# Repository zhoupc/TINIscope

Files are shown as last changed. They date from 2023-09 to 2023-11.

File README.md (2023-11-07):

# TINIscope 

<!-- **Tightly integrated neuronal imaging fluorescence microscope** -->

<!-- <img src="./assets/demo_video.gif" alt="animation of neural activity recorded in a mouse using the TINIscope" width="300" align="right" /> -->
simultaneous calcium imaging in 4 hippocampal regions of a mouse

In this project repository, we introduce TINIscope, a **Tightly Integrated Neuronal Imaging microscope** optimized for electronic and opto-mechanical design. With its compact and lightweight design of 0.43 g, TINIscope enables unprecedented simultaneous imaging of behavior-relevant activity in up to four brain regions in mice. Moreover, TINIscope can be combined with additional modules to facilitate optogenetics, electrical stimulation, or local field potential recordings, allowing for multi-modal experimental design. Overall, TINIscope represents a timely and indispensable tool for studying the brain-wide interregional coordination that underlies unrestrained behaviors.

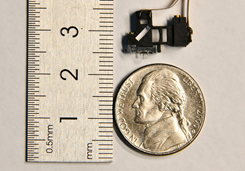
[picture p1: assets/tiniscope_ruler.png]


## Features

TINIscope features an ultra-compact size and an incredibly light weight, enabling the option to wear four of them on a single mouse. The key specifications are outlined below:

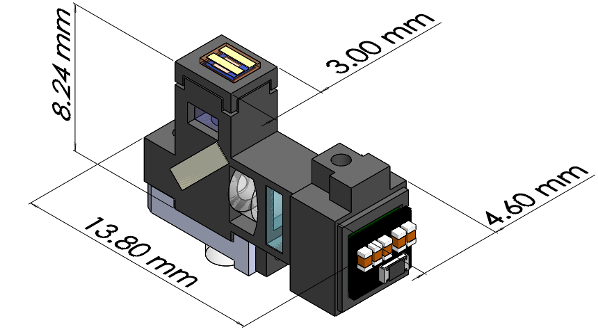
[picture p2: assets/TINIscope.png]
dimension of one TINIscope


| Specications                | Value            |
| --------------------------- | ---------------- |
| Field of view(FOV)          | 450 × 450  μm    |
| Weight of single unit       | 0.43g            |
| Dimensions                  | 4.6×13.8×8.24 mm |
| Typical oprating frame rate | 40 Hz            |
| Optical resolution          | 2.2 μm           |
| Adjustment of focal range   | ~0-200 μm        |
| Cable length                | 50/70 cm         |

## Overview 
As standalone equipment, TINIscope reaches a new level of miniaturization in head-mounted microscopes, reducing the burden added to smaller or developing animals like juvenile songbirds. Based on the TINIscope design, we further systematically developed an experimental paradigm, including multi-site implantations and a commutator for wire untangling, for multi-region calcium imaging in freely behaving mice. 

In this repository, our goal is to present our work in the development of optics, electronics, and mechanics pertaining to various aspects of TINIscope. We cover topics such as the lightpath, housing, baseplate, commutator system, and provide useful guidelines for conducting experiments. To access detailed information regarding each topic, please click on the provided links below.

A comprehensive summary of all parts were listed in [`part_list/TINIscope_Parts_List.xlsx`](./part_list/TINIscope_Parts_List.xlsx).

### TINIscope
* [Part list](./TINIscope_Documents/PartList_tiniscope.md)
* [Step-by-step assembly](./TINIscope_Documents/Assembly.md)

### Commutator system 
* [Guide](./TINIscope_Documents/Commutator.md)
### GUI and drivers 
* [Installation](./TINIscope_Documents/InstallGUI_driver.md)
### Experiment
* [Virtual simulation](./TINIscope_Documents/VirtualSimulation.md)

## Main contributors and institutions
* Feng Xue, xue0feng@ustc.edu.cn
* Fei Li, fei.li1@siat.ac.cn
* Ke-Ming Zhang, zkm037@ustc.edu.cn
* Pengcheng Zhou, zhoupc1988@gmail.com
* [University of Science and Technology of China 中国科学技术大学](https://www.ustc.edu.cn)
* [Xiongan Institute of Innovation 雄安创新研究院](http://xii.ac.cn/)
* [Shenzhen Institute of Advanced Technology](http://siat.cas.cn/)
## Declaration
[University of Science and Technology of China](https://www.ustc.edu.cn) has filed a patent application related to the design of TINIscope. 

## Acknowledgement 
* [MIniscope-v4](https://github.com/Aharoni-Lab/Miniscope-v4)
  * The UCLA miniscope team is a trailblazer in open-sourcing miniaturized microscope technologies. Their well-written and organized documentation has been a great inspiration for us to adopt similar styles when open-sourcing the development of our TINIscope.

<!-- ## Copyright -->

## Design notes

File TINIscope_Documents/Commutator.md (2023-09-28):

# Part list of commutator system 
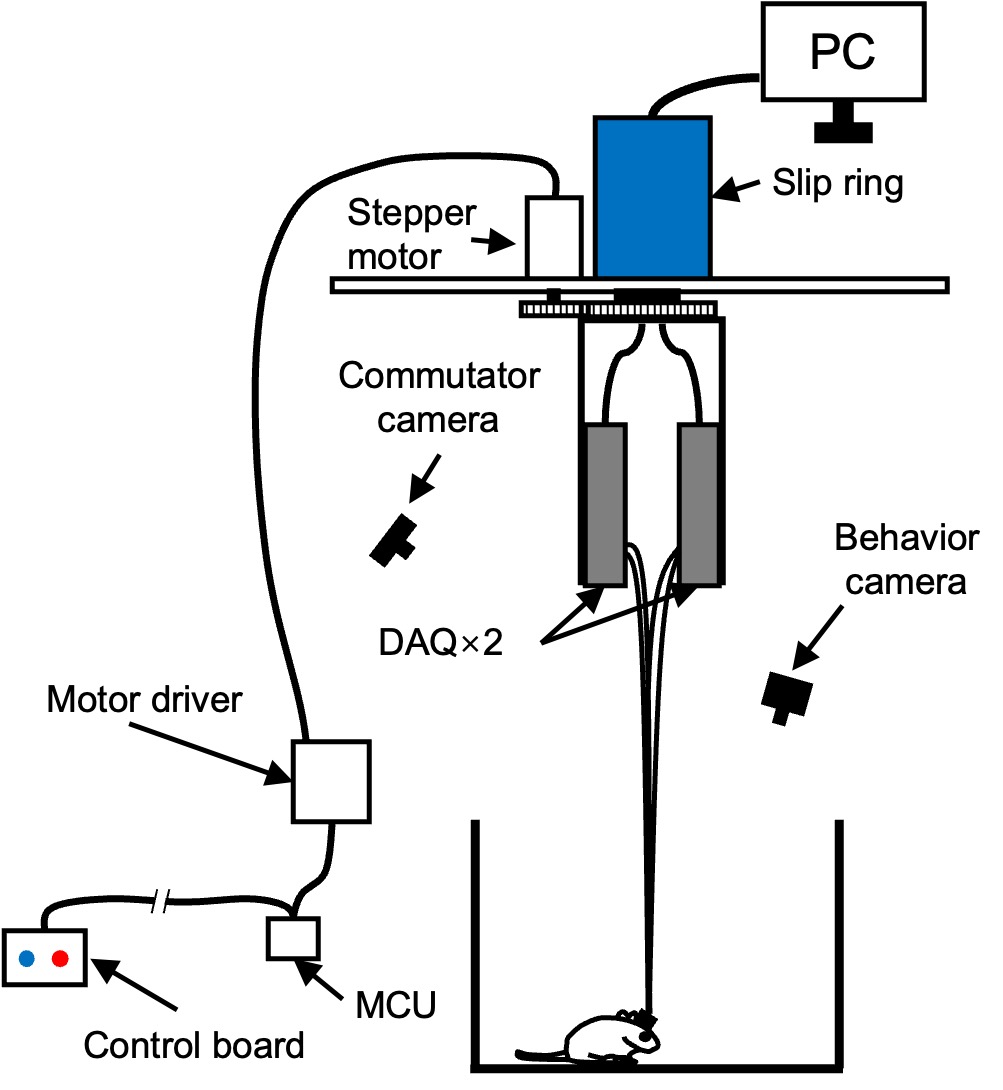
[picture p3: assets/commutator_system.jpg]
Diagram of the commutator system


The commutator employs a stepper motor to rotate an electrical slip ring and unravel any twisted cables according to their shapes monitored by a camera. 

<!-- DAQ boards were connected to a computer through a slip ring driven by a stepper motor, and the motor was manually controlled by the experimenter outside of the experimental room through the control board -->

<!-- Commutator design. The commutator was composed of a 3D-printed nylon U-shaped bracket, an electric slip ring (B1286-08S-4U-62641, Senring), a stepper motor (42B60, Taobao) with a driver (DM320, Taobao), and a controller (Arduino Nano, Supplementary. Two MIPI DAQ boards were mounted on the arms of the bracket, which was fixed to the rotor of the electric slip ring. The stepper motor was coupled to this rotor via a 1:2 gear set, providing the power to rotate the DAQ boards. During experiments, the experimenters determine the rotation direction by monitoring the shapes of flexible PCBs through a camera (Supplementary Figure 4A-C) and then press the controller to rotate the stepper motor clockwise or counterclockwise through the Arduino Nano, avoiding any movement-related wire entanglements. -->

## Part list 
### Motor driver 
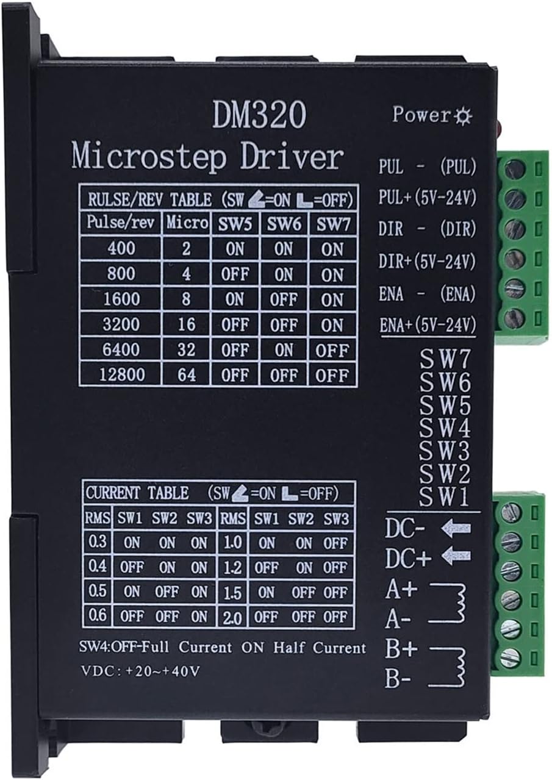
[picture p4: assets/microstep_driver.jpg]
motor driver


[DM320 2H320 Stepper motor driver controller](https://www.electric-b2c.com/products/dm320-2h320-stepper-motor-driver-controller-pulse-12800-microstep-motor-brushless-dc-motor-shell-for-28-35-42-stepper-drivers)
[](https://cdn.shopifycdn.net/s/files/1/0583/0872/2881/files/DM320_2H320_Stepper_motor_driver_controller.pdf?v=1660788999)

Product features: 
1. supply voltage: DC12-36V or AC12-24V 
2. Drive current: 0.3-2.0A 
3. subdivision precision: 1-128 subdivision options
4. opto-isolated signal input 
5. motor noise optimization function 
6. can drive any 2.0A below current 2-phase or 4-phase hybrid stepper motor 
7. 200KHz chop frequency

For more specifications, check the 
[data sheet](https://cdn.shopifycdn.net/s/files/1/0583/0872/2881/files/DM320_2H320_Stepper_motor_driver_controller.pdf?v=1660788999).
### Stepper motor 

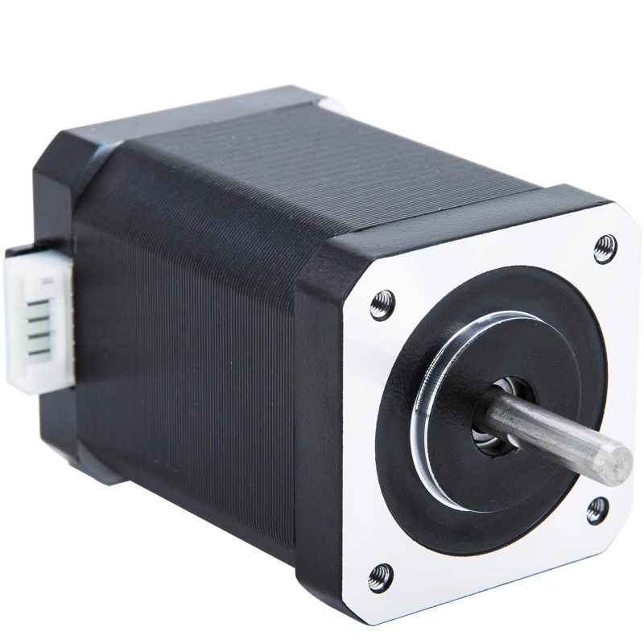
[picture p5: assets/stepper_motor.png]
stepper motor


[ML42HB60 J-4218HB4401 42 Stepper motor High 60mm Torque 0 89Nm Motor](https://www.yoycart.com/Product/521600244151/)

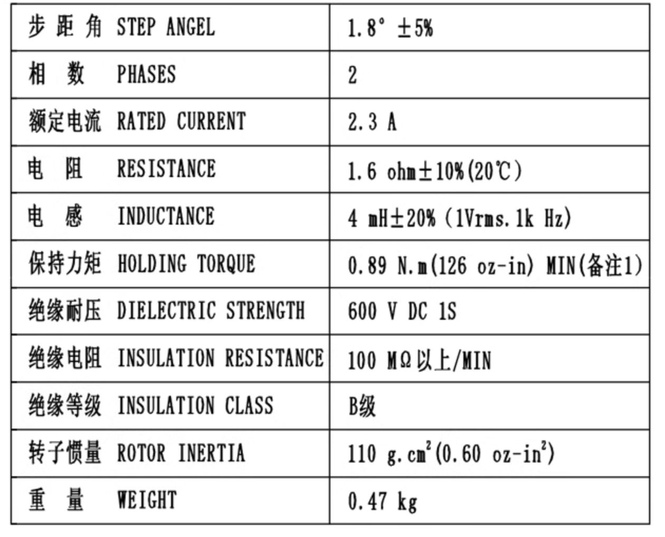
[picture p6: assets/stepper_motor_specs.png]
stepper motor


### slip ring 
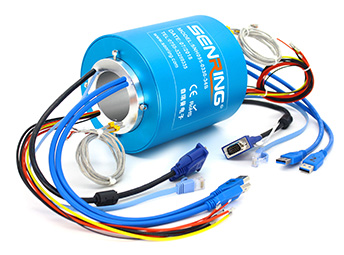
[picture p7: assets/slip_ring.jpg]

[BH1286 Series Industrial Bus Slip Rings](https://www.senring.com/industrial-bus/bh1286.html) 

**Features**:
 * hole size 12.7mm, OD 86mm,max. 96 circuits; 
 * accurately transmit high speed data 
 * stably transmit all kinds of signals, such as, RS-232, RS-485, RS-422, VGA, etc.; 
 * stably transmit all kinds of signals, such as, Profibus,LonWorks,CanBus,DeviceNet,ControlNet, etc.; 
 * transmit mixed signals, such as, USB,HDMI, 1000M ethernet, fiber optic, VGA, DVI, coaxial RF (high frequency), etc. 
 * stably transmit Ethernet data(10M / 100M / 1000M BaseT);

see more information form the [product catalog](https://www.senring.com/pdf/Senring-BH1286-Series-SlipRing-Catalog.pdf). 

### MCU 
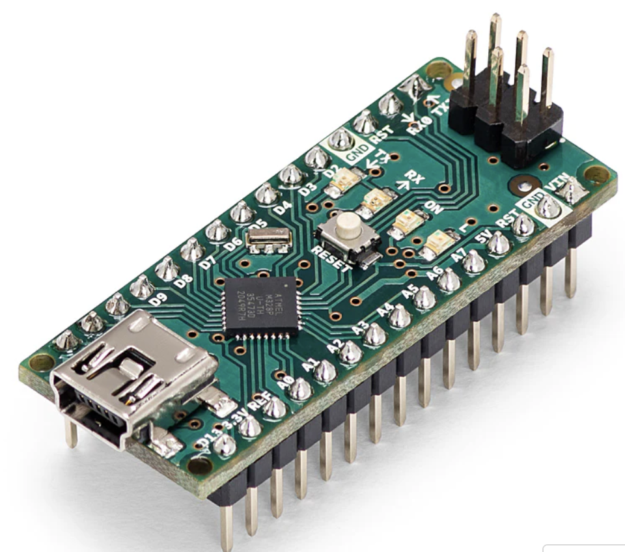
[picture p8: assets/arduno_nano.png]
arduno nao


[Ardonu Nano](https://store-usa.arduino.cc/products/arduino-nano?selectedStore=us)

The classic Arduino Nano is the smallest board to build your projects with.
Each of the 14 digital pins on the Nano can be used as an input or output, using pinMode(), digitalWrite(), and digitalRead() functions. They operate at 5 volts. Each pin can provide or receive a maximum of 40 mA and has an internal pull-up resistor (disconnected by default) of 20-50 kOhms. 

### control board 

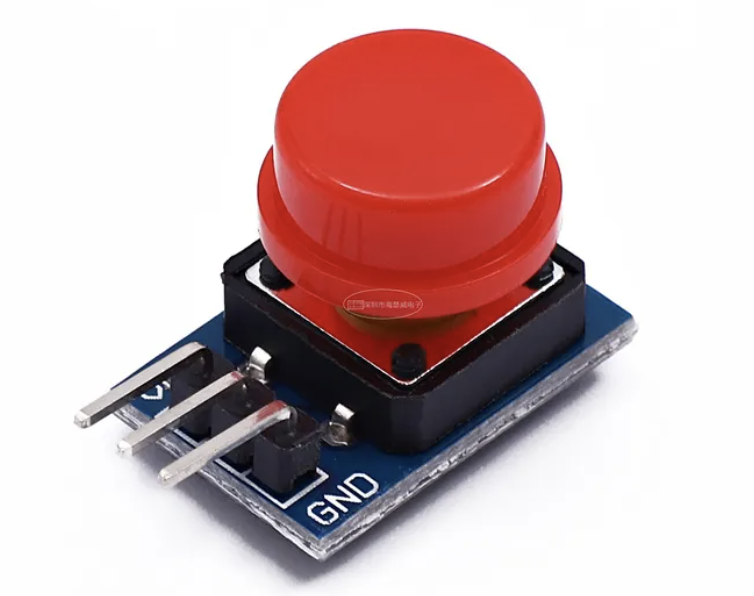
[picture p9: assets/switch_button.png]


The control board is composed of two switch button connecting to the MCU. 

### Commutator camera and behavior camera 

## Put them together 

Once you have acquired all the necessary components, assembling them is as straightforward as connecting them according to the diagram provided above. To give you a better idea of the final product, we have included a video demonstration below:

our commutator system

<!-- <video src="../assets/virtual_simulation.mp4" controls title="commutator"></video> -->

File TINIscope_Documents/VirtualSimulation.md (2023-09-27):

# Computater simulation for TINIscope implantation

When implanting multiple TINIscopes, it is essential to design proper equipment arrangements to avoid spatial conflicts and balance weight. To achieve this, Solidworks was utilized for simulating the implantation and determining optimal solutions through three steps. 
* **Firstly**, a standard 3D model of the whole mouse brain and targeted brain regions was downloaded from the [Allen Brain Atlas](https://download.alleninstitute.org/informatics-archive/current-release/mouse_ccf/annotation). 
  
* **Secondly**, the downloaded models and 3D model of TINIscopes were imported into Solidworks. 
  
* **Lastly**, the GRIN lens of each TINIscope was fixed to the target area, and the orientation of each TINIscope was adjusted to achieve the best arrangement. The final orientation of each TINIscope was then exported to guide surgical implantation.

virtual simulation

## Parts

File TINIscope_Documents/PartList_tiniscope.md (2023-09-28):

## Part list 

 <!-- For details on options of how to purchase/produce these components, go to the Part Procurement page of this wiki. -->

The core of TINIscope consists of a Rigid-Flex PCB, filter set, objective GRIN lens set, half-ball lens, and machined or printed housing, slider and baseplate. Below outlines the details of each of these components.
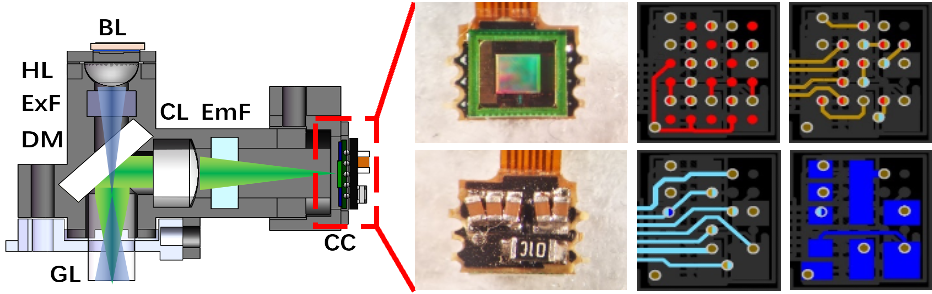
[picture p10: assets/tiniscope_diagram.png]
Section diagram of TINIscope


* BL: blue LED
* HL, half-ball lens
* ExF, excitation filter
* DM, dichroic mirror
* GL, GRIN objective lens
* CL, convex lens
* EmF, emission filter
* CC, CMOS camera.

<video src="../assets/tiniscope_parts.mp4" controls title="Title" width=400></video>
## Machined or Printer Parts 
The print and CNC files for the TINIscope housing and baseplate are located in the [TINIscope_Housing](../TINIscope_Housing/) folder of this repository.

Three parts were 3D printed using the Form 2 printer from formlabs, utilizing their normal black resin material. Additionally, testing was conducted with the Form 3 printer to achieve enhanced printing resolution while using the same material. Optional materials such as PU Rigid 1000/650 Resin, which offer improved durability according to their description, were considered. However, due to unavailability in our local area, we were unable to purchase these materials for testing purposes.

The baseplate is CNC machined.

### Body
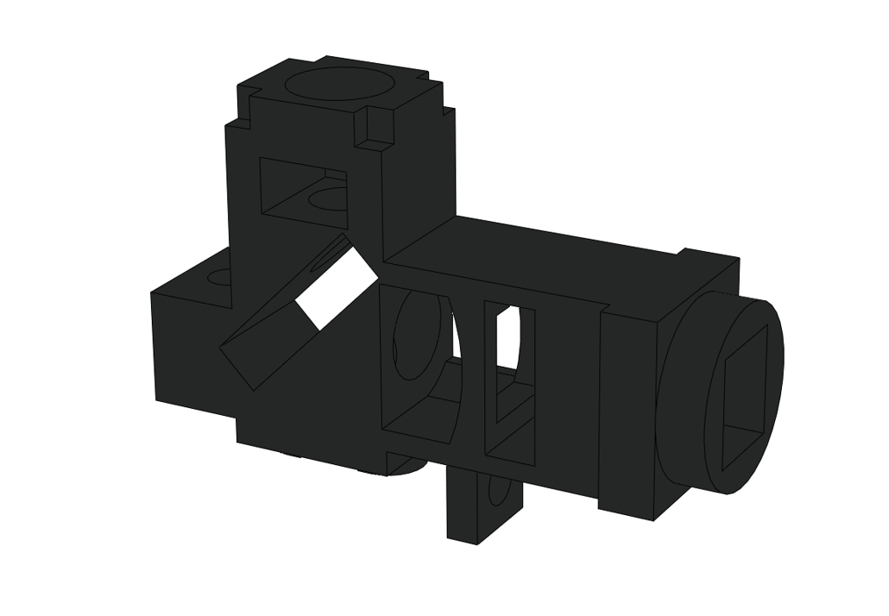
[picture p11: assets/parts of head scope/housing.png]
body

The main body of TINIscope fits all the optical parts. A intruction will help to illustrate how to assemble it with these optical parts, pleaase refer to the [Step-by-step assembly](./Assembly.md).
<br><br>

### Slider
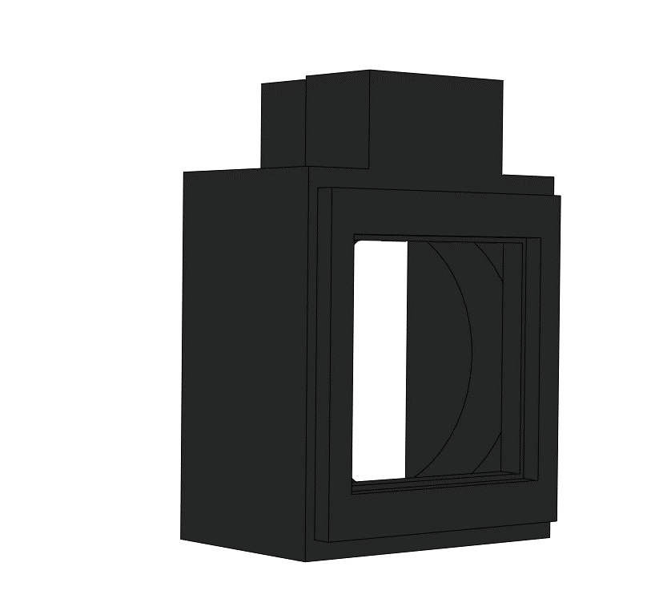
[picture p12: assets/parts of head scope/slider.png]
slider

The slider serves the purpose of accommodating the CMOS image sensor and aligning with the body to enable focal plane adjustments for the TINIscope. A wider range of focal plane adjustment can be achieved by utilizing a longer slider range. The slider features a hole designed to fit an M1 self-tapping screw, which helps secure it to the body once the focal plane adjustment is complete.

### Led cap
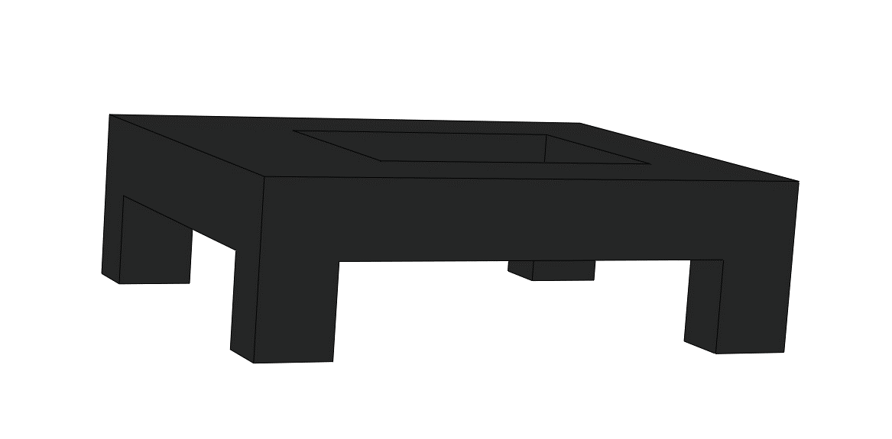
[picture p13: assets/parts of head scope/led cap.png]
led cap

The precise positioning of the hall ball lens and LED is crucial for ensuring an optimal illumination path. To maintain the accurate placement of the LED, a led cap is used after correctly positioning the hall ball lens in the middle of the illumination path.

### Baseplate
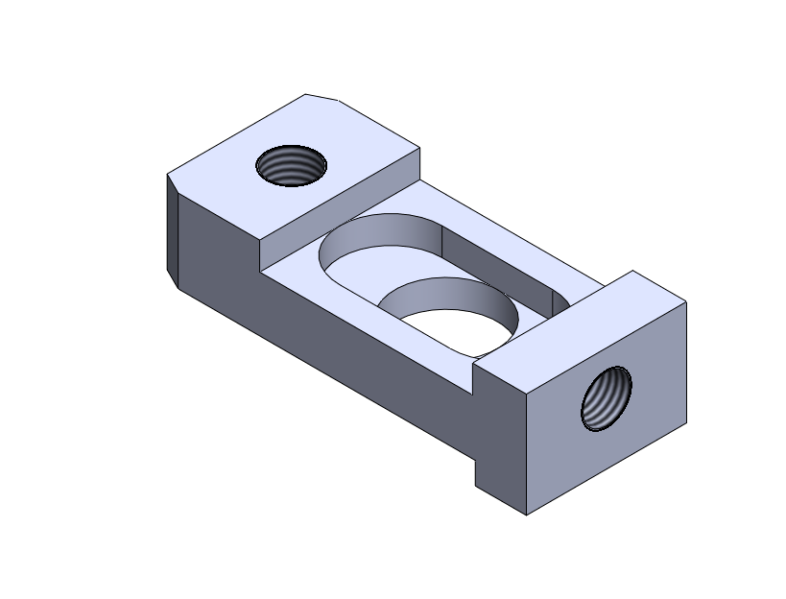
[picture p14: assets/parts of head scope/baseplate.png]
baseplate

The baseplate is primarily CNC machined to ensure the durability of its two M1 screw threads. Additionally, the hole for fitting the GRIN objective lens is designed with high precision to achieve optimal image quality.
<br><br>

## PCB 
The fabrication files for the TINIscope PCB can be found in the [TINIscope_PCB](../TINIscope_PCB/) folder of this repository. 

### Rigid-flex PCB 
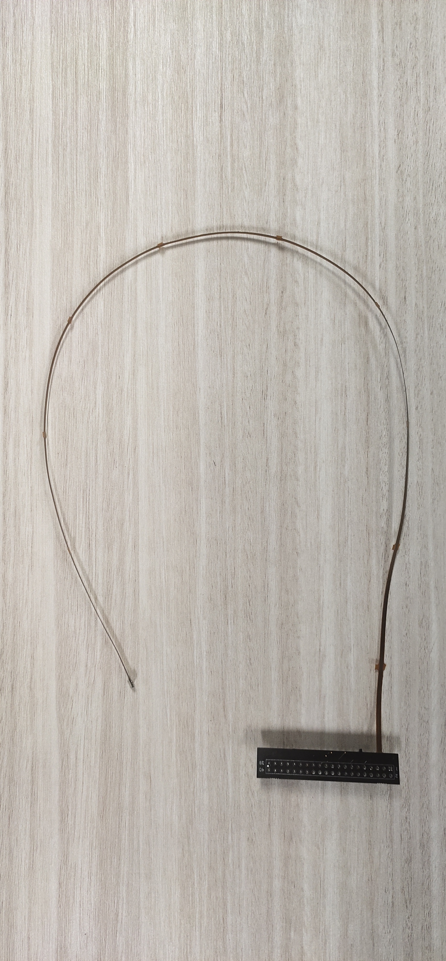
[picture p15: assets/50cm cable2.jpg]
50cm cable


To establish a connection between the CMOS image sensor and DAQ board, a rigid-flex PCB is created. The flex cable portion of the PCB is designed to be 50/70 cm in length, ensuring flexibility when the animal moves freely. It is crucial to follow strictly to the layer stack excel file to maintain both stable data transmission and accommodate the animal's agility simultaneously.

The Bill of Materials (BOM) includes all the essential components required to be soldered onto this PCB. Once these components are soldered onto the PCB, four PCBs will be connected to two DAQ boards. Subsequently, these two DAQ boards will be securely mounted on the 3D printed U-shaped Bracket.

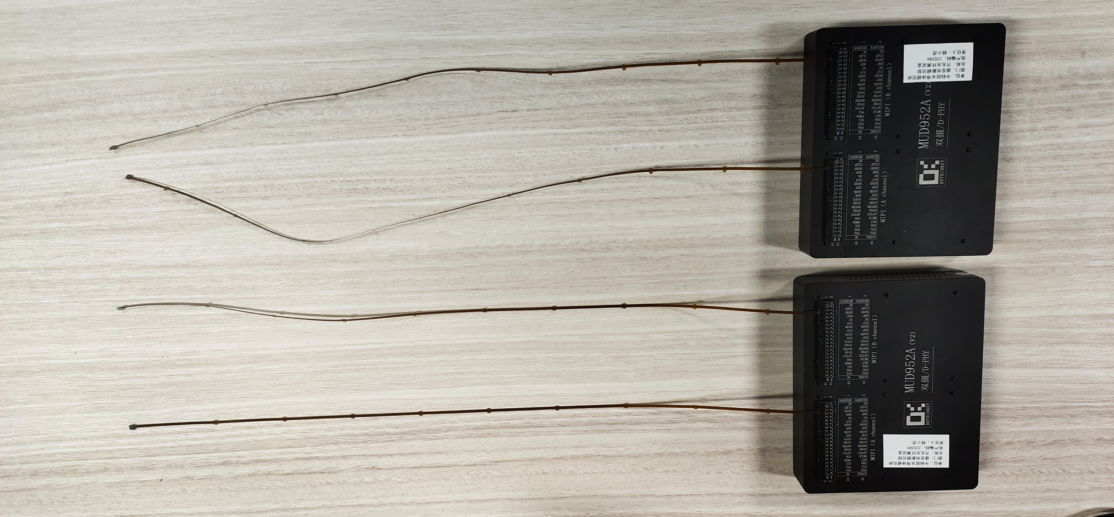
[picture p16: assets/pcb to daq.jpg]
pcb to daq


### FPC for LED
This FPC is for a easier solder of LED twisted pair. The twisted pair should be as thinner as possible to keep the agility of animal.

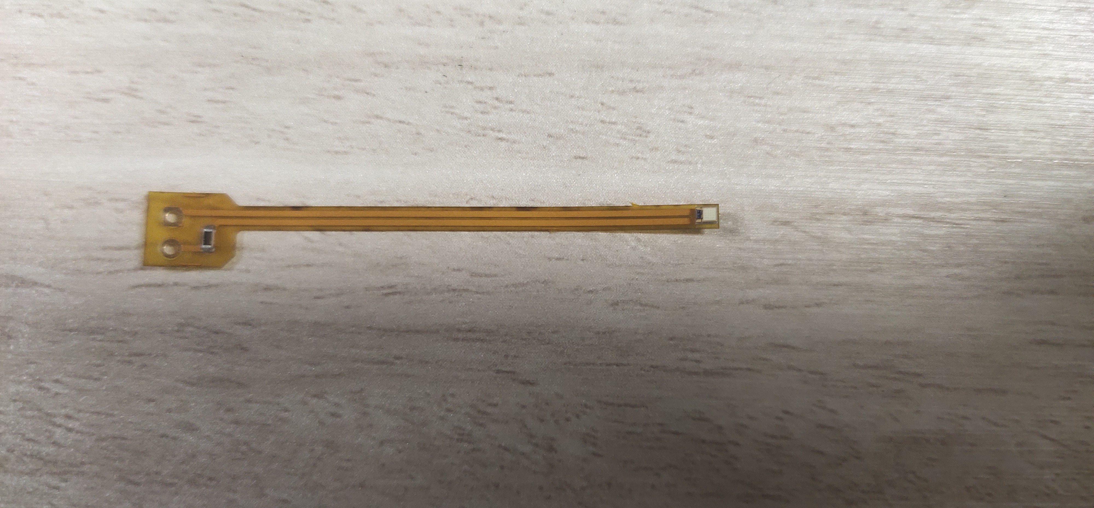
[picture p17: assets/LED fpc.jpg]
LED fpc
 twisted pair

## Optical parts
### Half ball lens
half ball lens
The diamiter of half ball lens is 2 mm. This part can be purchased from:

* Edmund optics
* #45-933

### Excitation filter
excitation filter
The size of excitation filter is diced to 2.8 * 1.8 mm. This part can be purchased from:

* Chroma
* ET470/40x

The size of it can be customized at Chroma, or be diced off at Sunlight-tech from a complete filter.
### Dichroic mirror
dichroic mirror
The size of dichroic mirror is diced to 2.8 * 4 mm. This part can be purchased from:

* Chorma
* 59002bs

The size of it can be customized at Chroma, or be diced off at Sunlight-tech from a complete filter.
### GRIN objective lens
GRIN objective lensr
The VIS coating of this lens can help to deal with the stray light. This part can be purchased from:

* Edmund optics
* 64#537
### Plano-convex lens
dichroic mirror
This part can be purchased from:

* Edmund optics
* #88-775
### Emission filter
emission filter
The size of emission filter is diced to 2.8 * 3 mm. This part can be purchased from:

* Chorma
* ET525/50m

The size of it can be customized at Chroma, or be diced off at Sunlight-tech from a complete filter.

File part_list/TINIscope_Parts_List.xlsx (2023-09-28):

List of Head Mounted Scope Components
TINIscope 3D Printing and CNC Parts
Quantity | Part Number | Suggested Vendor | Description | Link | Approximate Cost(each) | Notes
4 | MainBodyv2.3.2 | formlabs | High performance 3D printer | https://formlabs3d.cn/ | $0.07
4 | FocusSlider2.3.1 | formlabs | High performance 3D printer | https://formlabs3d.cn/ | $0.04
4 | led_cap | formlabs | High performance 3D printer | https://formlabs3d.cn/ | $0.03
4 | Metal Baseplate | Wenext | The baseplate of microscope | https://www.wenext.com/ | $30.27
Optical Components
Quantity | Part Number | Suggested Vendor | Description | Link | Approximate Cost(each) | Notes
4 | 45-933 | Edmund Optics | Half-ball lens | https://www.edmundoptics.cn/p/20mm-diameter-n-bk7-half-ball-lens/6434/ | $50.52
4 | ET470/40x | Chroma | 2.8*1.8mm | https://cn.chroma.com/products/parts/et470-40x | $10.31
4 | 59002bs | Chroma | 4.1*2.8mm | https://cn.chroma.com/products/parts/59002bs | $12.57
4 | 88775 | Edmund Optics | Diameter:3mm, Center width after symmetrical cutting on both sides:2.5mm | https://www.edmundoptics.cn/p/30mm-dia-x-45mm-fl-yag-bbar-coated-plano-convex-lens/35980/ | $78.39
4 | ET525/50m | Chroma | 3.0*2.8mm | https://cn.chroma.com/products/parts/et525-50m | $14.29
10/20 | 64537 | Edmund Optics | GRIN objective lens | https://www.edmundoptics.cn/p/18mm-dia-670nm-dwl-00mm-wd-vis-coated-grin-lens/19249/ | $79.55
10 | CLHS100GFT003 | Go!Foton | GRIN relay lens | https://www.gofoton.com/ | $88.39
1 | 36427 | Edmund Optics | NOA 68 | https://www.edmundoptics.cn/p/1-oz-application-bottle-of-noa-68/4178/ | $44.13
Electrical Components
Quantity | Part Number | Suggested Vendor | Description | Link | Approximate Cost(each) | Notes
4 | OV6211 | OmniVision | Low Power and Compact CameraChip Sensor | https://www.omnivision-group.com/search-haowei?text=ov6211 | $5.48
20 | c0402 | ickey | Capacitor (Semiconductor SIM Model) | https://www.ickey.cn/detail/1003001424772766/CC0402ZRY5V5BB105.html | $0.0019 each(100pk)
4 | r0603 | ickey | Resistor | https://www.ickey.cn/detail/1003001442960909/RC0603JR-0710KL.html | $0.0058 each(50pk)
4 | r0603 | ickey | Resistor | https://www.ickey.cn/detail/1003001222442274/RK73H1JTTD10R0F.html | $0.0024 each(50pk)
4 | HDR2X20 | Taobao | 2.54mm pin header | https://item.taobao.com/item.htm?id=632733944070&ns=1&abbucket=20 (https://item.taobao.com/item.htm?spm=a230r.1.14.62.2f3c29afplcr3W&id=632733944070&ns=1&abbucket=20) | $0.0301 each(100pk)
4 | LXZ1-PB01 | ickey | excitation LED | https://www.ickey.cn/detail/1003001444854928/LXZ1-PB01.html#01816da2-0a0d-4bfa-af8a-dcab9fa6923a | $1.5688 each(70pk)
2 | led_driver | Taobao | led_driver | https://detail.tmall.com/item.htm?_u=kaj248od2f2&id=17204422349&skuId=4375995072639 | $67.70
1 | twisted pair | Taobao | twisted pair | https://item.taobao.com/item.htm?spm=a1z09.2.0.0.2e6c2e8d4TeueZ&id=561021644525&_u=hb2qdiab912 | $17.78
Circuit Board
Quantity | Part Number | Suggested Vendor | Description | Link | Approximate Cost(each) | Notes
4 | Circuit Board | FASTPRINT | PCB | https://www.chinafastprint.com | $276.9223 each(10pk)
4 | Led Board | FASTPRINT | PCB | https://www.chinafastprint.com | $6.83905 each(10pk)
Screws
Quantity | Part Number | Suggested Vendor | Description | Link | Approximate Cost(each) | Notes
4 | M0.5 | Taobao | Screws | https://item.taobao.com/item.htm?spm=a312a.7700824.w4002-1246146503.12.699b2799aBMnc1&id=18725794469 | $0.10
4 | M1 | Taobao | Screws | https://item.taobao.com/item.htm?spm=a312a.7700824.w4002-1246146503.12.36b527ceIYhXoK&id=25683372879 | $0.10
DAQ and Behavior Camera
Quantity | Part Number | Suggested Vendor | Description | Link | Approximate Cost(each) | Notes
2 | MUD952 | Dothinkey | DAQ - Data acquisition board | http://www.dothinkey.com/ | $1712.95
2 | JHSM36s | Taobao | Behavioral camera and unwinding camera | https://item.taobao.com/item.htm?spm=a1z09.2.0.0.67002e8dJYHgiK&id=574186006401&_u=jb2qdia645a | $103.60 | One camera records the unwinding, the other records the behavior
Commutator
Quantity | Part Number | Suggested Vendor | Description | Link | Approximate Cost(each) | Notes
1 | B1286-08S-4U-62641 | senring | Electric slip ring | https://www.senring.cn/ | $202.81 | Electric slip ring
1 | 42HB60 | Taobao | Stepper motor | https://item.taobao.com/item.htm?spm=a1z09.2.0.0.67002e8dJYHgiK&id=522852381003&_u=jb2qdia3f10 | $7.54 | Stepper motor
1 | DM320 | Taobao | Motor Driver | https://item.taobao.com/item.htm?spm=a1z10.3-c-s.w4002-21805955586.9.2db426f4MmVixa&id=522854033607 | $12.33 | Microstep Driver
1 | Arduino Nano | Arduino | MCU | https://www.arduino.cc/ | $23.02 | Controller
2 | Button | Taobao | Buttons on the control board | https://item.taobao.com/item.htm?id=648041409997&ns=1&abbucket=6 (https://item.taobao.com/item.htm?spm=a21n57.1.0.0.7ba1523ckztAzI&id=648041409997&ns=1&abbucket=6) | $0.35
1 | Gear set | Wenext | 3D printed gears | https://www.wenext.com/ | $8.42
1 | U-shaped bracket | Wenext | 3D printed bracket | https://www.wenext.com/ | $21.51

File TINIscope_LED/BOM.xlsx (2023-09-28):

Comment | Description | Designator | Footprint | LibRef | Quantity
LED0 | Typical INFRARED GaAs LED | D1 | LXZ1_PB01 | LED0 | 1
Header 2 | Header, 2-Pin | P1 | HDR1X2 | Header 2 | 1
Res3 | Resistor | R1 | J1-0603 | Res3 | 1

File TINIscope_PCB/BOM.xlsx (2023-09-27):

Comment | Description | Designator | Footprint | LibRef | Quantity
OV6211 | image sensor | U1 | OV6211 | OV6211 | 1
1uF | Capacitor (Semiconductor SIM Model) | C1, C4, C5, C6, C8 | 0402 | Cap Semi | 5
MUD952 | connector | P1 | HDR2X20 | HM300 | 1
10K | Resistor | R2 | 0603r | Res2 | 1

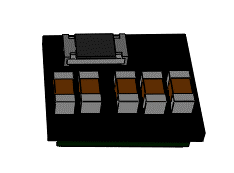
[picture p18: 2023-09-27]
assets/parts of head scope/CMOS sensor.png

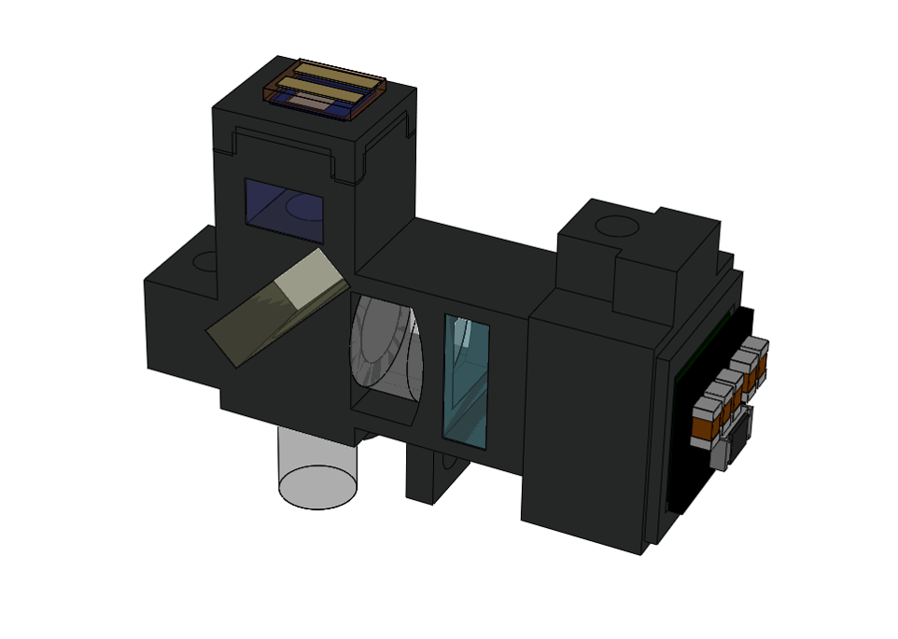
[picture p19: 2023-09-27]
assets/parts of head scope/图片12.png

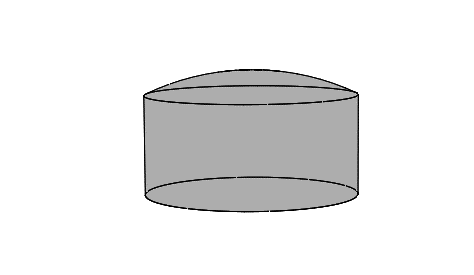
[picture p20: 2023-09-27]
assets/parts of head scope/plano convex lens.png

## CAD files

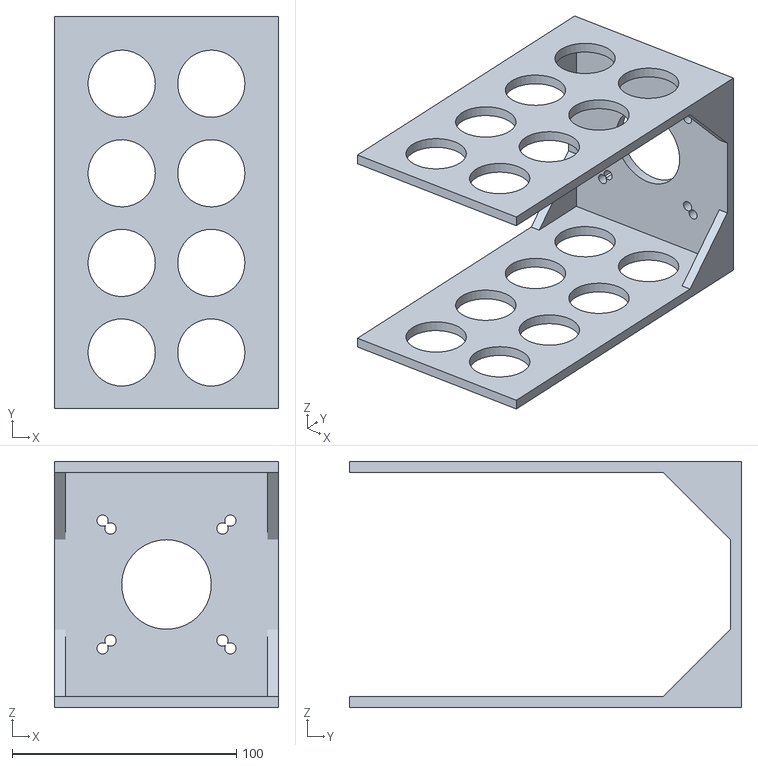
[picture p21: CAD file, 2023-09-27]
TINIscope_Commutator/U-shaped bracket.STL
100.0 x 175.0 x 110.0

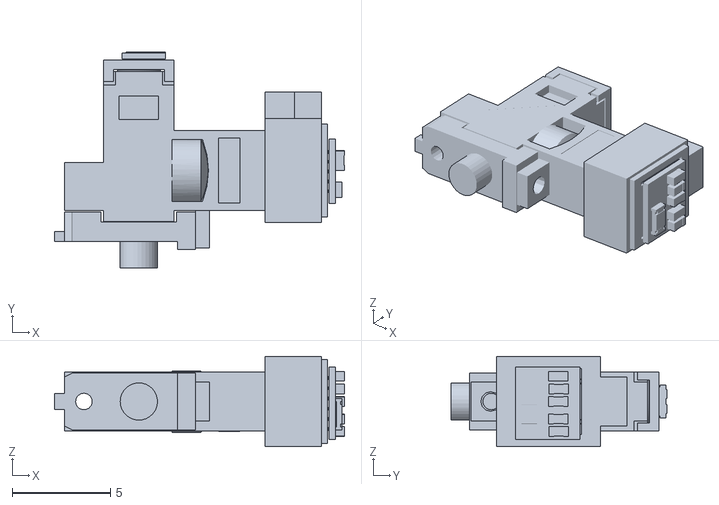
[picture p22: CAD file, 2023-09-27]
TINIscope_Housing/dummy TINIscope.STL
14.8 x 11.0 x 4.60

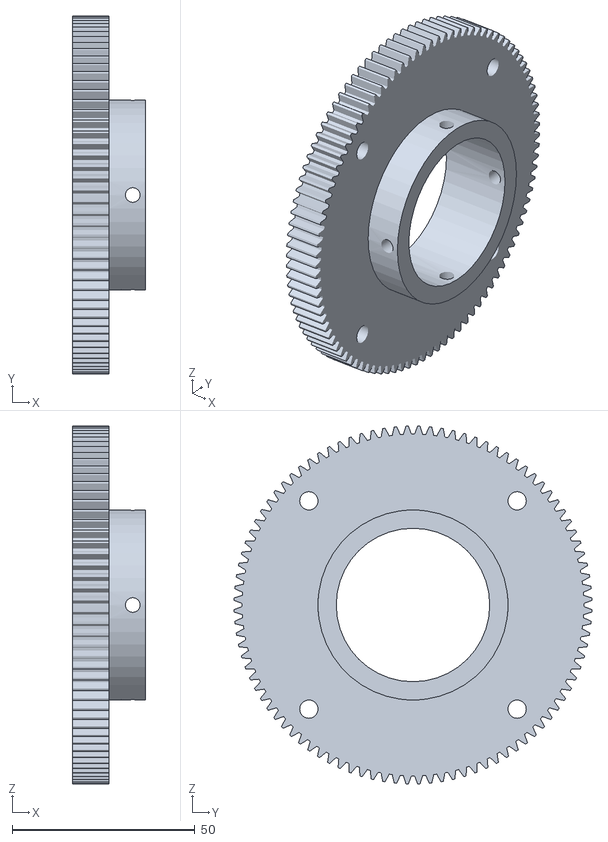
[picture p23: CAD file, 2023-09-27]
TINIscope_Commutator/gear of slip ring.STL
20.0 x 98.0 x 98.0

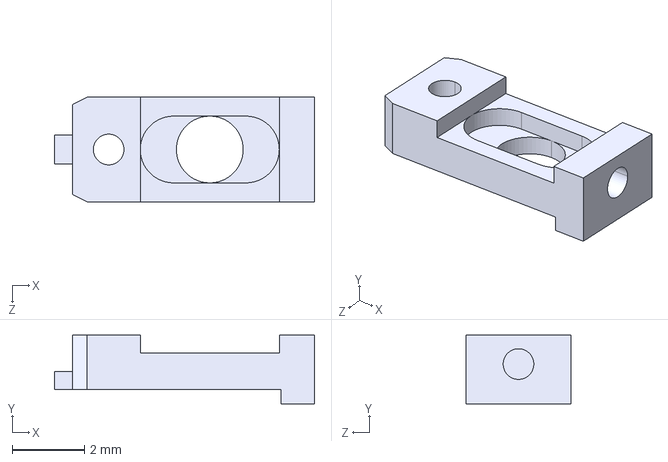
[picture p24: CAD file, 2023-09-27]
TINIscope_Housing/baseplate.STEP
7.20 x 1.90 x 2.90 mm

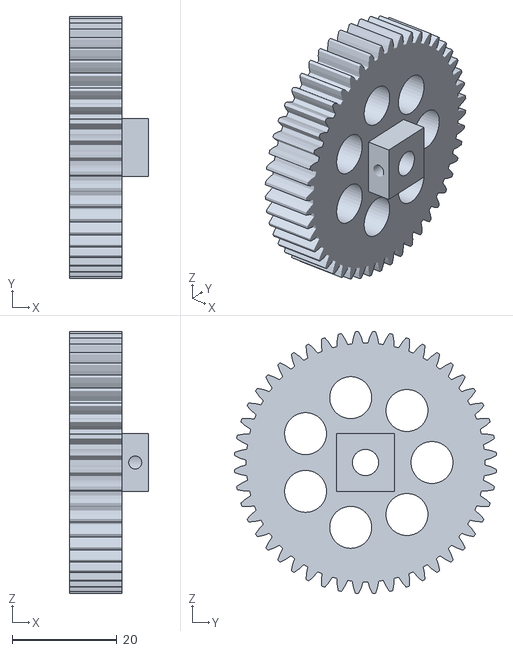
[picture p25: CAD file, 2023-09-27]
TINIscope_Commutator/gear of stepper motor.STL
15.0 x 49.9 x 49.9

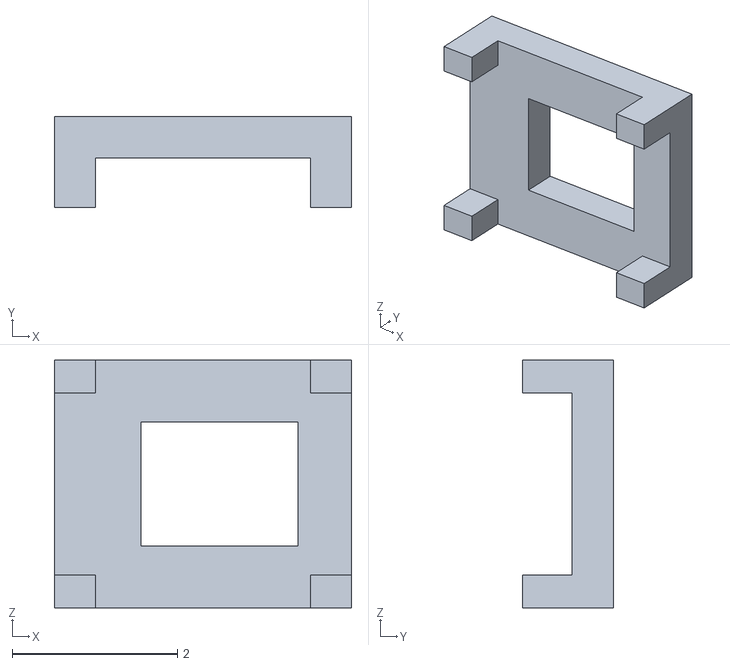
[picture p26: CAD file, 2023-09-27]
TINIscope_Housing/led_cap.STL
3.60 x 1.10 x 3.00

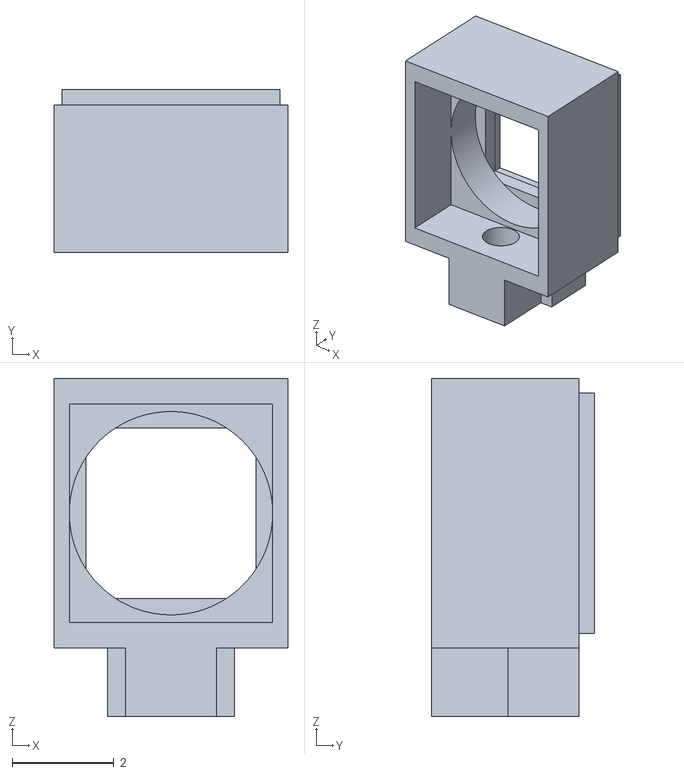
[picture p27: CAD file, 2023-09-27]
TINIscope_Housing/slider.STL
4.60 x 3.20 x 6.65

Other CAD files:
TINIscope_Housing/baseplate.STL

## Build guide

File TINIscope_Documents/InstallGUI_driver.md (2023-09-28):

# Install GUI and driver 

TINIscope uses a serialized data transmission protocol (MIPI interface) to send CMOS signals to the data acquisition (DAQ) board. This protocol does not require a serializer chip on the head-mounted side, but it needs 10 wires in total for data transmission, SCCB hardware configurations and power supply. The DAQ board not only receives CMOS signals from the rigid-flex PCB but also provides the power and clock signals directly, allowing the removal of these modules from the head-mounted side. 

For connecting the DAQ boards to the computer, USB connections are used. We have also developed a GUI software that facilitates acquiring image data and configuring the CMOS image sensors exclusively through the HDI rigid-flex PCB. Additionally, our GUI enables synchronization of the behavior camera with TINIscope recording.

In this section, we will provide a detailed description of how to configure the software environment for recording with TINIscope.

## Requirements
* The computer's RAM should be a minimum of 64GB
  * Given the throughput of 4 TINIscope devices at approximately 2B x (640 × 480) x 40 Hz x 4 ~ 93.75 MB/second, it is necessary to have a large RAM for optimal performance. 
* Windows operating system
  * Our testing has been conducted on the Windows operating system exclusively. 
* Driver for TINIscope 
  * Download the [zip file](../TINIscope_Softwares/driver.zip)
  * uncompress driver.zip.
* GUI software 
  * Download the [zip file](../TINIscope_Softwares/GUI.zip)
  * uncompress GUI.zip.

## Driver for TINIscope
Each TINIscope requires a separate USB3.0 connection from the DAQ board to connect to an individual computer. If the driver is not installed, the device will be identified as unrecognized in the Windows Device Manager. The file structure of uncompressed `driver.zip` is like below: 
```plain 
USB3.0_Kit_driver
├── x64
│   ├── WdfCoInstaller01009.dll
│   ├── dtusb3.cat
│   ├── dtusb3.inf
│   ├── dtusb3.sys
│   ├── dtusb3x64.cat
│   └── dtusb3x64.sys
└── x86
    ├── WdfCoInstaller01009.dll
    ├── dtusb3.cat
    ├── dtusb3.inf
    └── dtusb3.sys
2 directories, 10 files
```

Here are steps for installing the driver: 

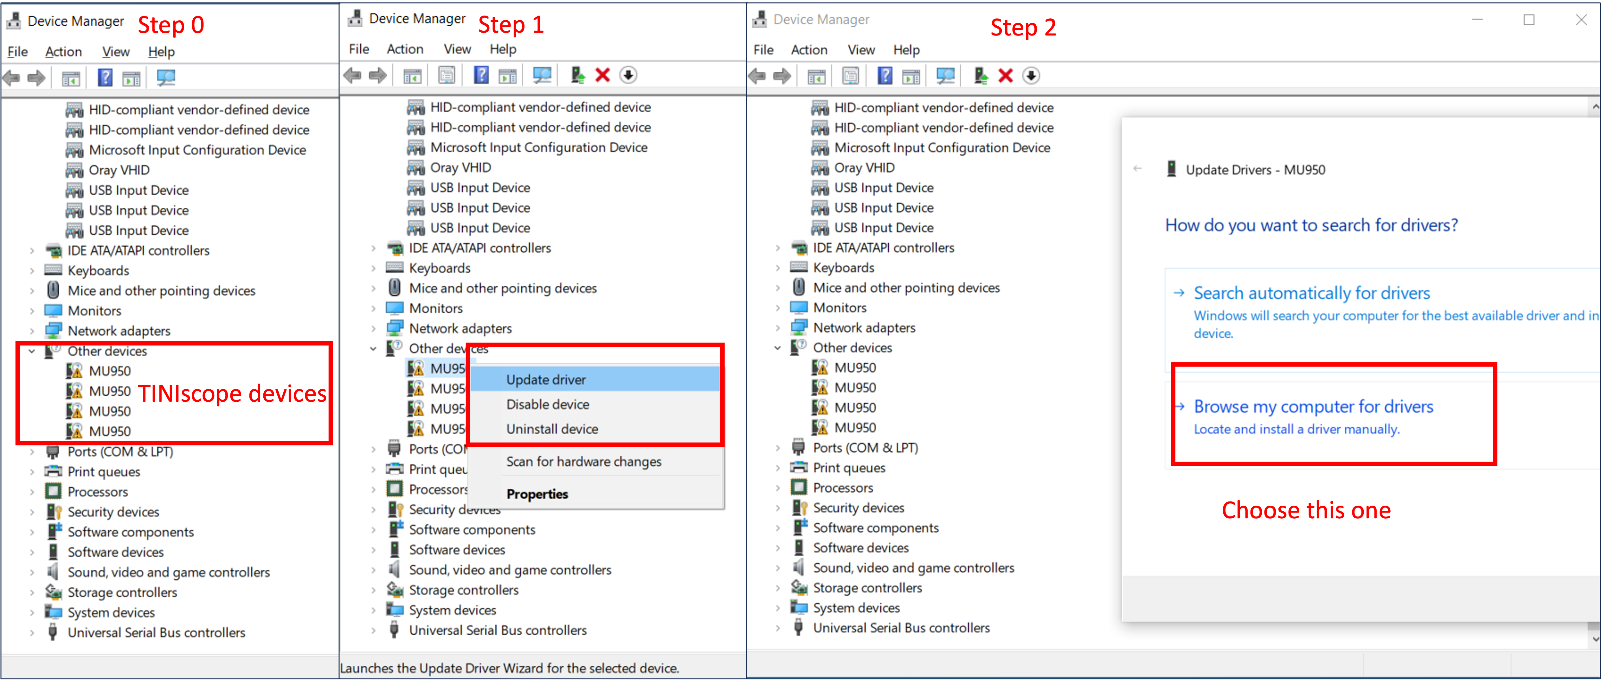
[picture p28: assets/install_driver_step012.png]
steps 0/1/2 of driver installation


* step 0: open Device Manager in Windows and find the 4 unrecognized TINIscope devices, labelled as MU950. 
* step 1: right click one of them and choose **update driver**. 
* step 2: in the pop up window, choose **browse my computer for drivers**. 
* step 3: select either `x64` or `x86` folder according to your operating system in the uncompressed `USB3.0_Kit_driver` folder. 
* step 4: repeat the same operation for the other 3 decices. 

Congratulations to you if see the following:

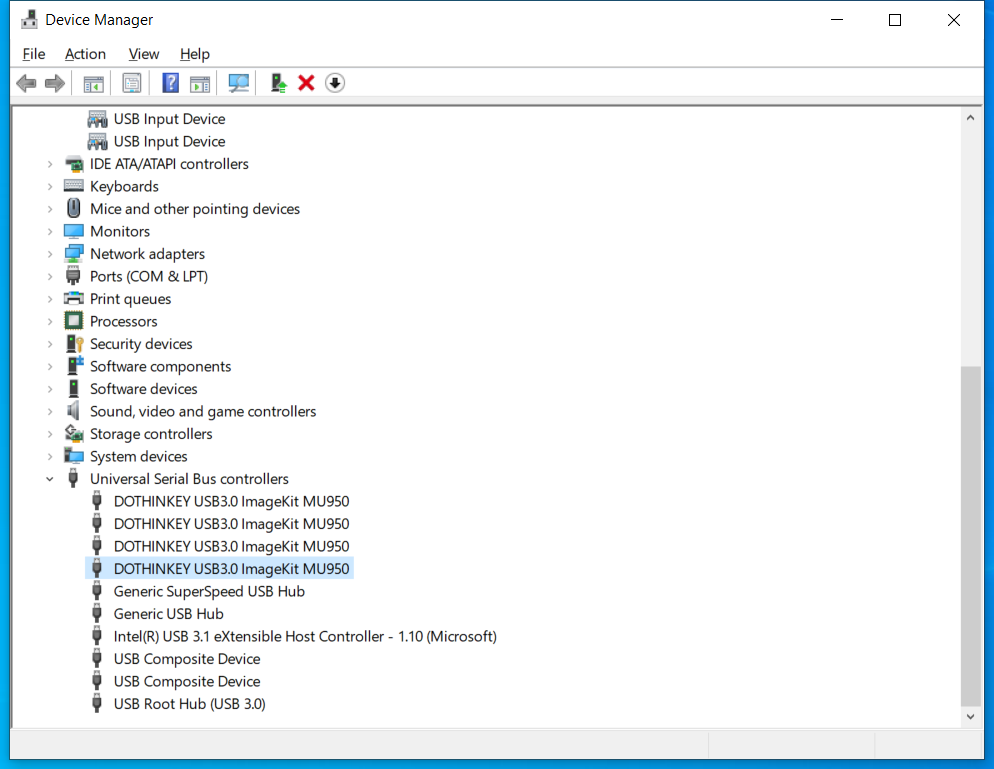
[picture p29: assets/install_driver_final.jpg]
driver installation done


## GUI 
These GUI software programs can be executed directly without requiring any installation.The file structure of the uncompressed `GUI.zip` is shown below: 
``` plain 
GUI
├── DTDualMipiOnlyDemo-1.1.4.exe
├── DTDualMipiOnlyDemo-1.1.4.*.         ## skipped files 
├── *.dll.                              ## skipped dll files 
├── OV6710_2L_400_063_20 - 副本.ini.     
├── OV7251_480_063_c0.ini
├── controller
│   ├── DTDualMipi-Qt-1.0.4-rc1.exe
│   ├── *.dll                           ## skipped dll files 
│   ├── plugins

2 directories, 50 files
```
Among these files, we mainly use 3 of them:
* `DTDualMipiOnlyDemo-1.1.4.exe`
* `OV7251_480_063_c0.ini`
* `controller/DTDualMipi-Qt-1.0.4-rc1.exe`

Essentially, the process involves two primary steps, which are outlined in the following sections.

### Configuring TINIscopes with DTDualMipiOnlyDemo-1.1.4.exe 

1. By double-clicking on `DTDualMipiOnlyDemo-1.1.4.exe` twice, two separate windows for TINIscope configuration will open simultaneously, as depicted below:
   
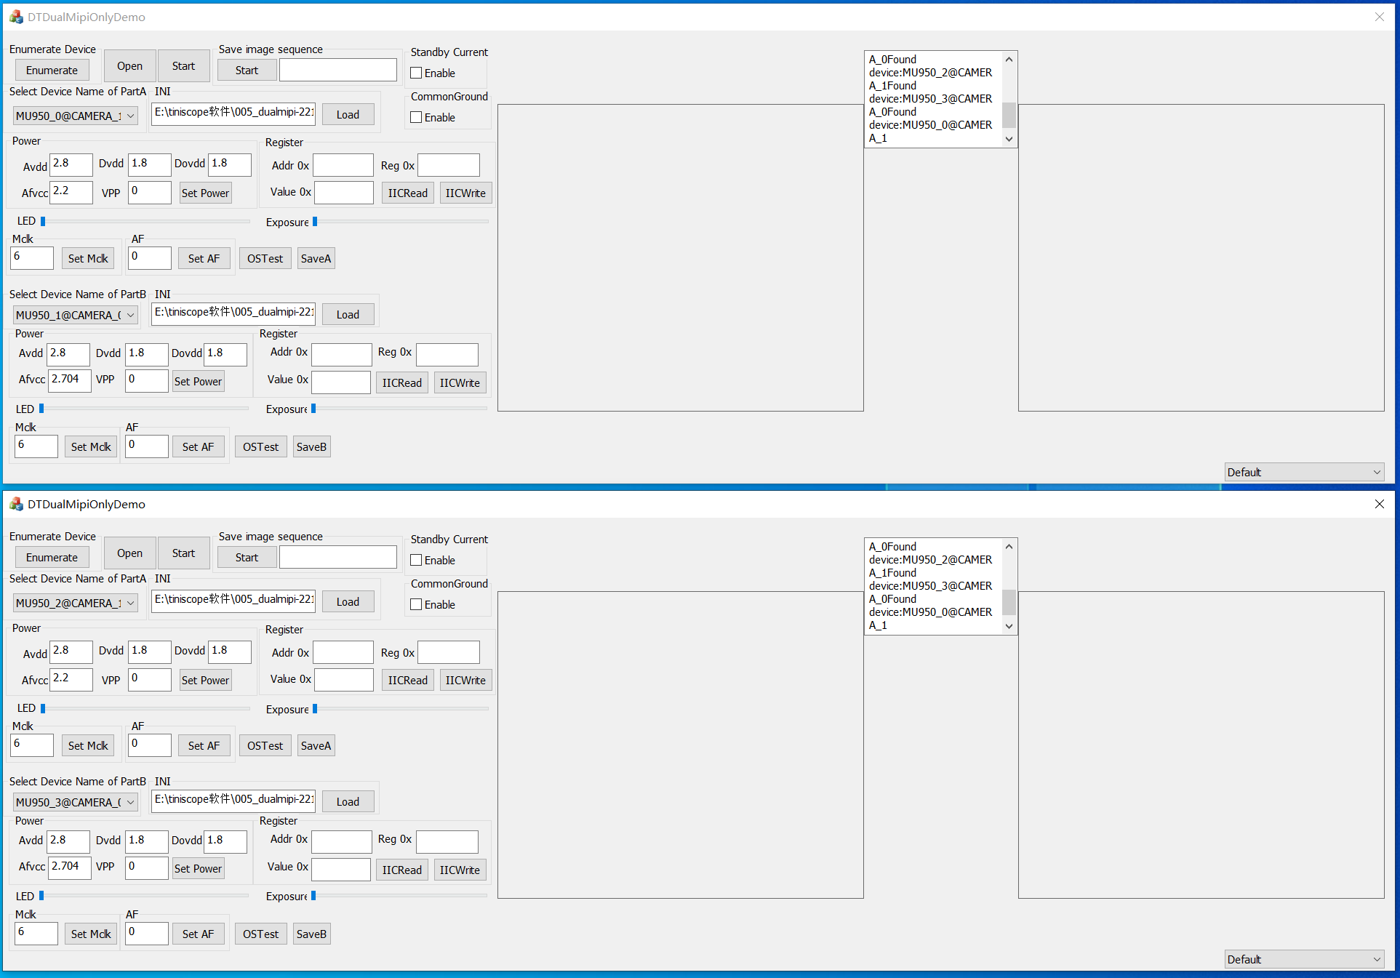
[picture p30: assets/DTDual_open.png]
   
2. Each window manages two TINIscope devices, and it is necessary to manually select one device for each slot.

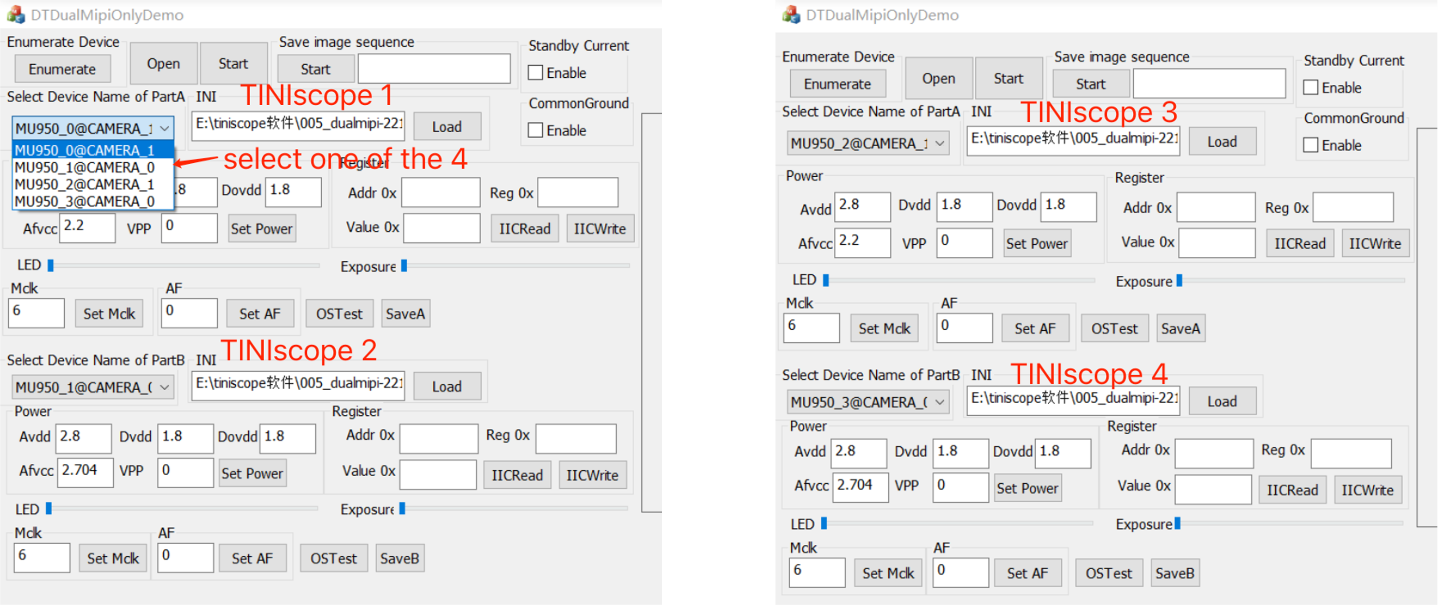
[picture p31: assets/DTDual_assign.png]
    

3. load configuration files by clicking the `Load` button and adjust the options. 
   The description of these options were shown in this table 
   |name | descriptions|
   |-----| ------------|
   |Avdd| power for analog circuit of CMOS, default: 2.8 V | 
   |Dvdd| not used|
   |Dovdd| power for I/O circuit of CMOS, default: 1.8|
   |Afvcc| adjust for LED brightness, range 2.2V-3.0 V |
   |VPP | |
   |Addr 0x| CMOS, 12C address; | 
   |Reg 0x| register address of CMOS; 0x3501 | 
   |Value 0x | for example time of CMOS, range: 0-0x1b, i.e., 0-27|
   |Mclk| clock of CMOS|
   |AF | not used |
   || |

4. Verify the status of TINIscope configuration by clicking the button `Open` on the top panel. 
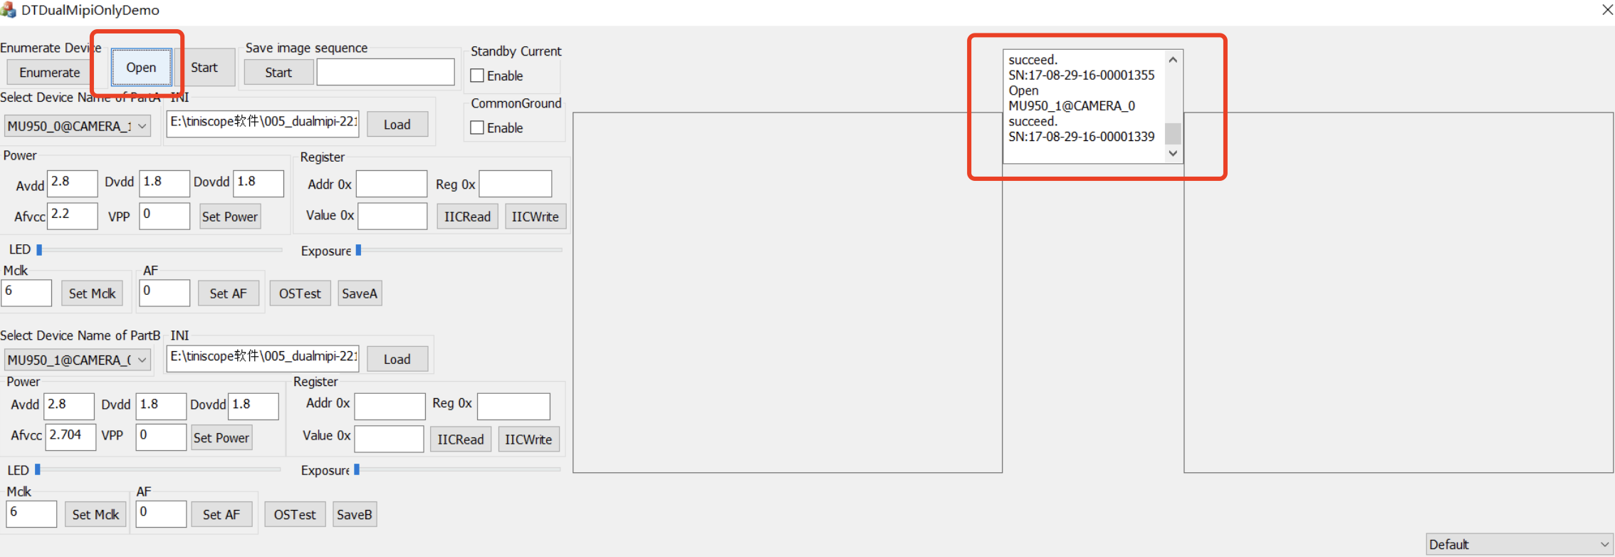
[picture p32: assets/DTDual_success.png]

Congratulations to you if you see two `succeed` in one window.

### Synchroning calcium imaging and behavior recording with controller/DTDualMipi-Qt-1.0.4-rc1.exe

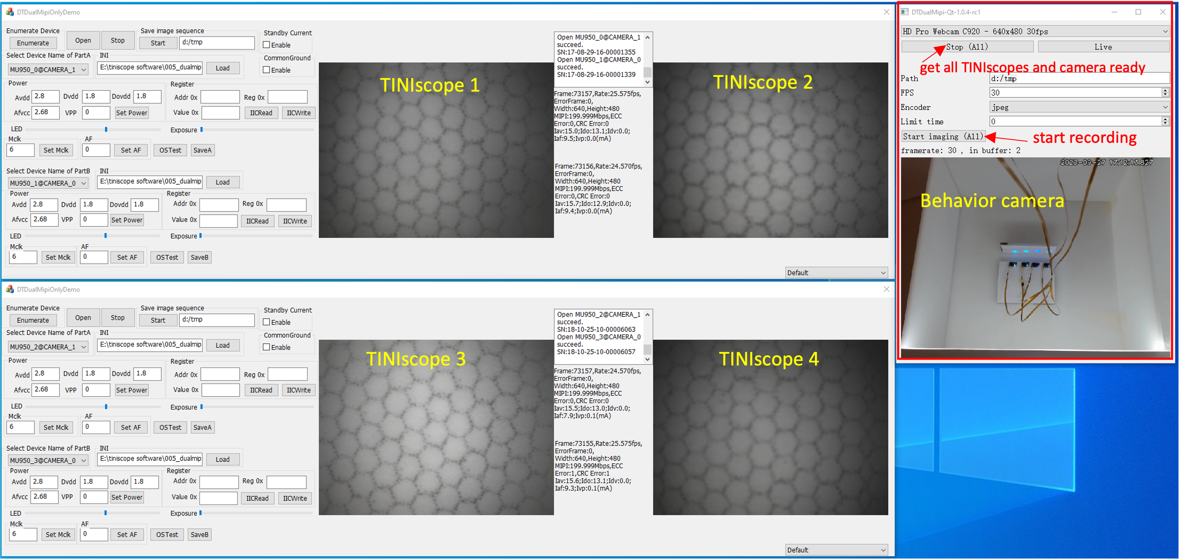
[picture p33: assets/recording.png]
screenshot of calcium imaging and behavior recording


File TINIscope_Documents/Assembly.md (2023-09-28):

# Assembly guide for TINIscope
This is the brief instruction of how to assemble the head mounted microscope of TINIscope.

Before started you should prepare for all the parts necessary to assemble it, please refer to the [Part list](.PartList_tiniscope.md).

Please keep all the optical parts clean. 

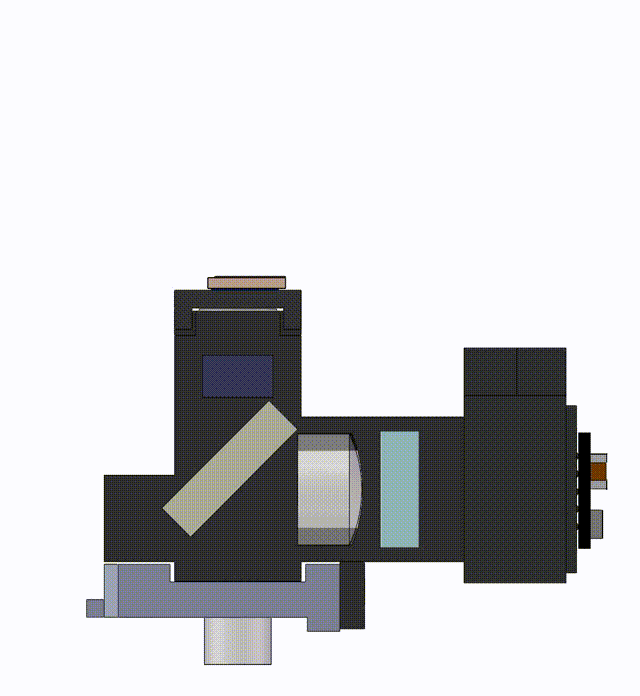
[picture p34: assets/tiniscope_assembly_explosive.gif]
animation of neural activity recorded in a mouse using the TINIscope


## Assembly steps 
### Step 1
Insert the dichroic mirror to the body.

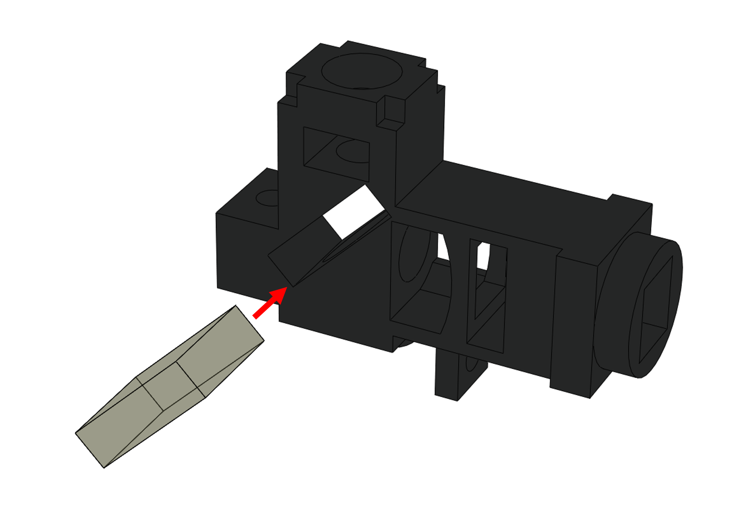
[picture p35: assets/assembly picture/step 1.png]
step1


### Step 2
Insert the excitation to the body.

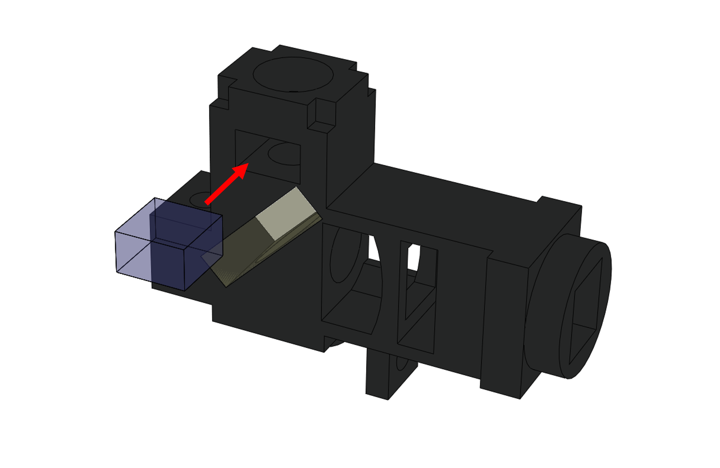
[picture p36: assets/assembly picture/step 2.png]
step2


### Step 3
Place the half ball lens on the upside of the body.

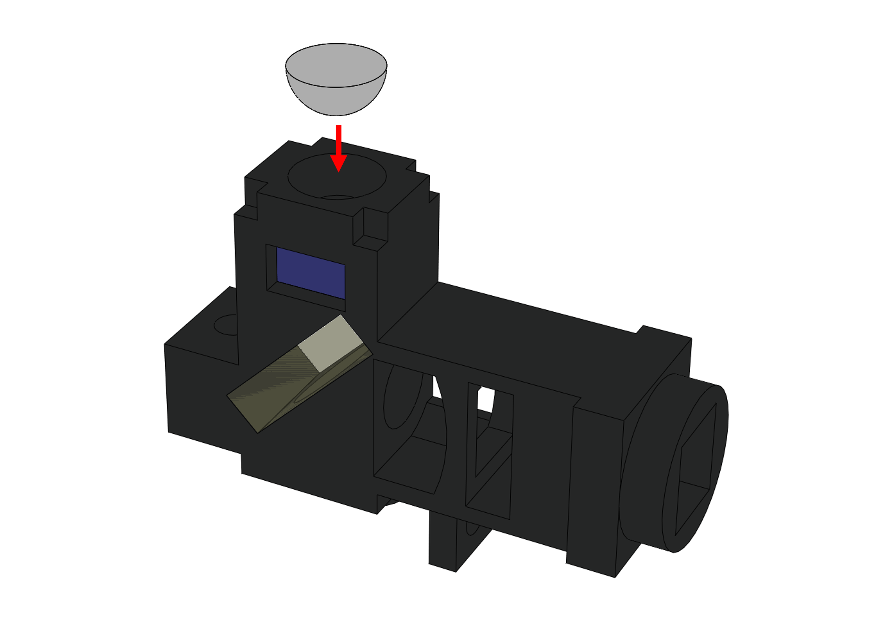
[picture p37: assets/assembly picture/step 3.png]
step3


### Step 4
Insert the plano-convex lens to the middle of the body.

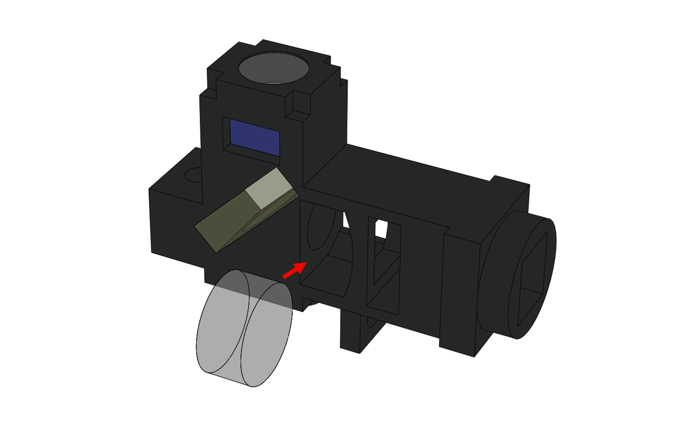
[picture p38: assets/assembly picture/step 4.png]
step4


### Step 5
Insert the emission filter to the body.

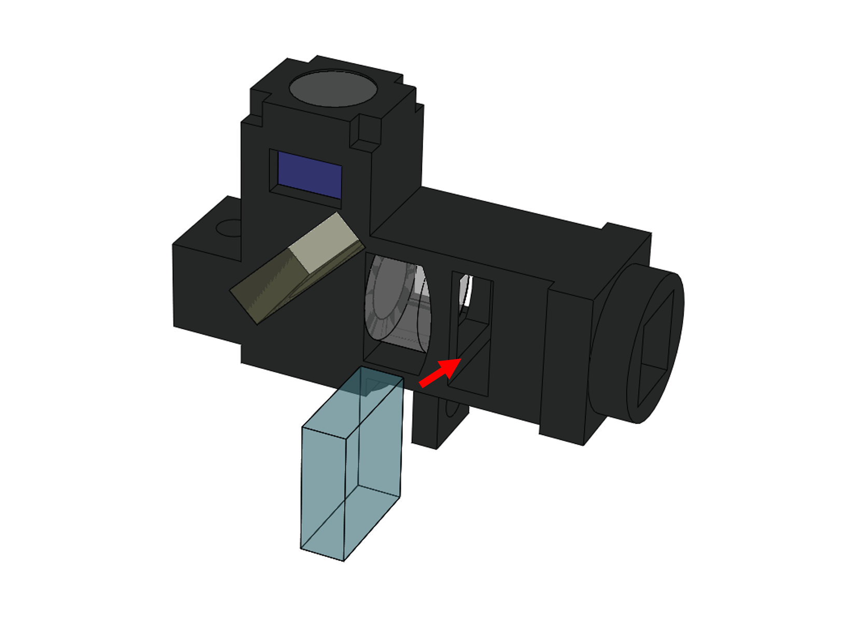
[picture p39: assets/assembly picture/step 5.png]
step5


### Step 6
Mate the slider to the body.

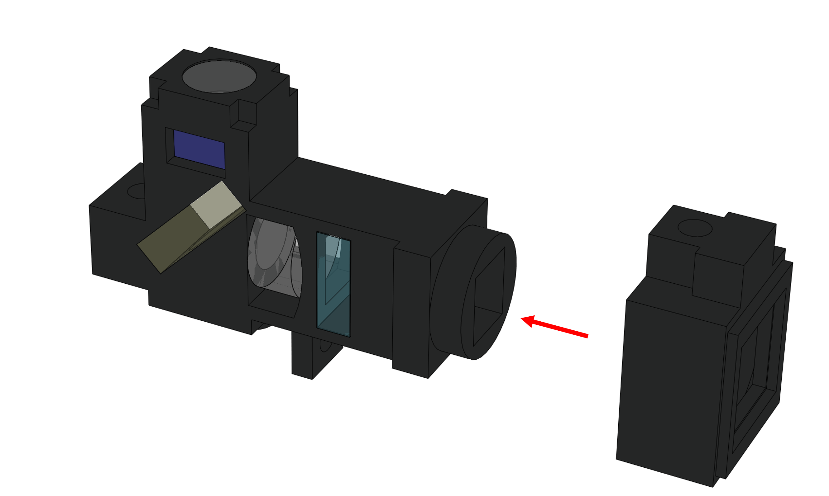
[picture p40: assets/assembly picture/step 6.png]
step6


### Step 7
Attach the CMOS image sensor PCB to slider, and then glue them together.

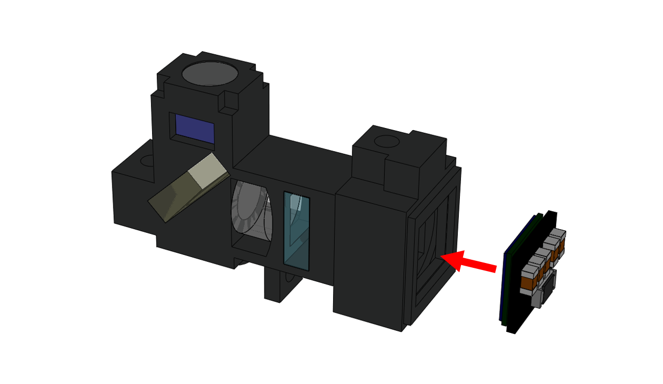
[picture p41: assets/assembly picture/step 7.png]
step7


### Step 8
Place the LED cap.

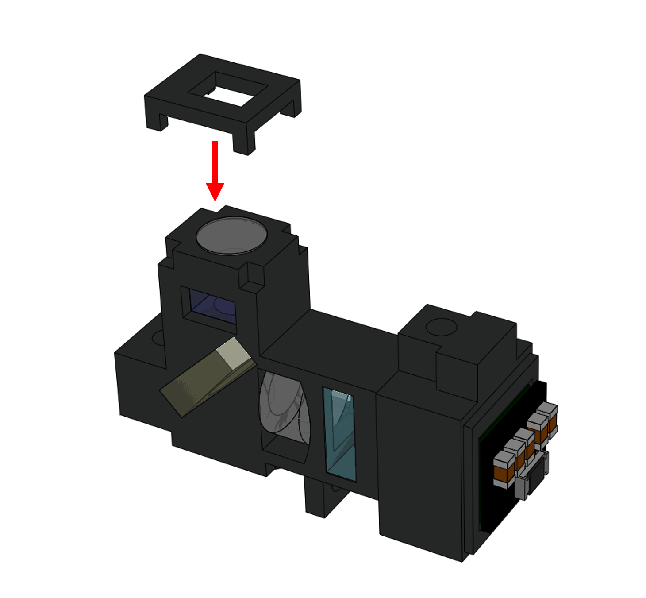
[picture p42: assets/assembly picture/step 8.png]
step8


### Step 9
Place the LED, and then glue LED, LED cap and the body module with adhesive.

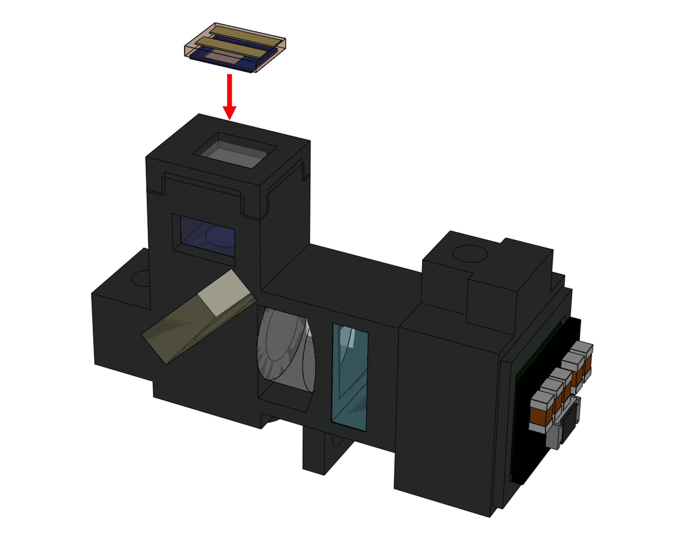
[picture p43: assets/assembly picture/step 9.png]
step9


### Step 10
Insert the GRIN objective lens.

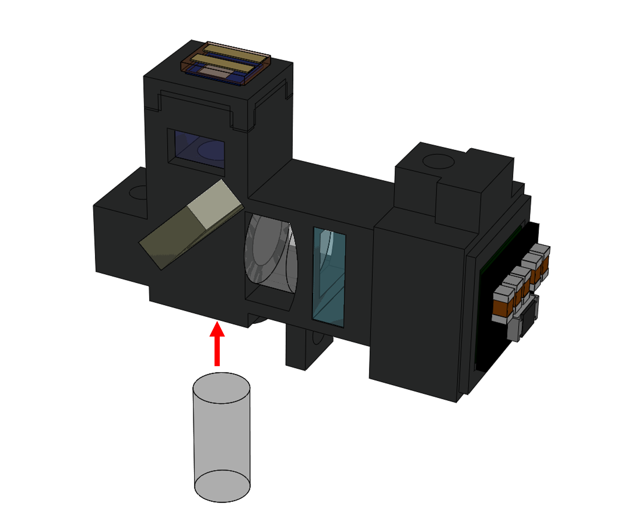
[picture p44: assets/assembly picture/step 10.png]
step10


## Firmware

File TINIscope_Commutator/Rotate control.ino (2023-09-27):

int rightin=2;
int leftin=3;
int rl=4;
int m=5;

void setup() {
  // put your setup code here, to run once:
pinMode(rightin,INPUT);
pinMode(leftin,INPUT);
pinMode(rl,OUTPUT);
pinMode(m,OUTPUT);
}

void loop() {
  // put your main code here, to run repeatedly:
if(digitalRead(rightin)==HIGH){
  digitalWrite(rl,HIGH);
  for(int i=0;i<1280;i++){
    digitalWrite(m,HIGH);
    delayMicroseconds(10);
    digitalWrite(m,LOW);
    delayMicroseconds(10);
  }
}
if(digitalRead(leftin)==HIGH){
  digitalWrite(rl,LOW);
  for(int i=0;i<1280;i++){
    digitalWrite(m,HIGH);
    delayMicroseconds(10);
    digitalWrite(m,LOW);
    delayMicroseconds(10);
  }
}
}

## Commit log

2023-09-27 add hardware
    [BOM.xlsx, TINIscope_v1.GBL, TINIscope_v1.GBO, TINIscope_v1.GBP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]
2023-09-28 revise TINIscope parts and assembly
2023-09-28 update LED and part list
    [BOM.xlsx, led_v1.GBL, led_v1.GBS, led_v1.GKO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]
2023-09-28 part list
    [TINIscope_Parts_List.xlsx]
